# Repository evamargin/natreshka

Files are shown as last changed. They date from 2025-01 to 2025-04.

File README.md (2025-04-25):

# Natreshka - Neuropixels 2.0 implant ([pdf](https://github.com/evamargin/natreshka/blob/main/Natreshka%20-%20Neuropixels%202.0.pdf))

## 1. Introduction

**Natreshka** is an open-source implantation system designed for Neuropixels 2.0, offering a secure, modular, and user-friendly solution for chronic recordings. The implant is lightweight (3.8 g), compact (14.6 × 14.2 × 26 mm), and fully 3D-printable, requiring only standard M1/M3 screws and nuts. Beyond its minimalistic design, Natreshka enables easy manual implant assembly, fast and precise implantation under different angles, manual **stereotax-free** probe recovery, and protected storage of assembled probes (Fig. 1). Successfully tested in freely moving gerbils and rats, Natreshka streamlines implantation procedures, reduces surgery time, and enhances animal welfare, making it an efficient and accessible tool for neuroscience research.

This guide will take you through every step - from printing and assembling to implantation and recovery - while highlighting pitfalls and offering practical tips for a smooth operation.

<p align="center">
  Figure 1
</p>

**Figure 1.** Our view.

- [1. Introduction](#1-introduction)
- [2. Materials and equipment](#2-materials-and-equipment)
  - [2.1. List of printed and sourced parts](#21-list-of-printed-and-sourced-parts)
    - [2.1.1. Parts list (3D printed)](#211-parts-list-3d-printed)
    - [2.1.2. Parts list (non-printed)](#212-parts-list-non-printed)
  - [2.2 Tools Required](#22-tools-required)
    - [2.2.1. Recommended 3D printers, filaments](#221-recommended-3d-printers-filaments)
    - [2.2.2. Assembly tools](#222-assembly-tools)
- [3. 3D printing the components](#3-3d-printing-the-components)
  - [3.1. 3D printing setting](#31-3d-printing-setting)
  - [3.2. Post-Printing Processing](#32-post-printing-processing)
- [4. Natreshka’s lifecycle](#4-natreshkas-lifecycle)
  - [4.1. Build a payload](#41-build-a-payload)
  - [4.2. Assemble](#42-assemble)
    - [4.2.1. Prepare the parts](#421-prepare-the-parts)
    - [4.2.2. Assemble the implant](#422-assemble-the-implant)
    - [4.2.3. Prepare the cable](#423-prepare-the-cable)
  - [4.3. Implant](#43-implant)
  - [4.4. Record](#44-record)
  - [4.5. Recover](#45-recover)
    - [4.5.1. Clean](#451-clean)
  - [4.6. Store](#46-store)

## 2. Materials and equipment

### 2.1. List of printed and sourced parts

<p align="center">
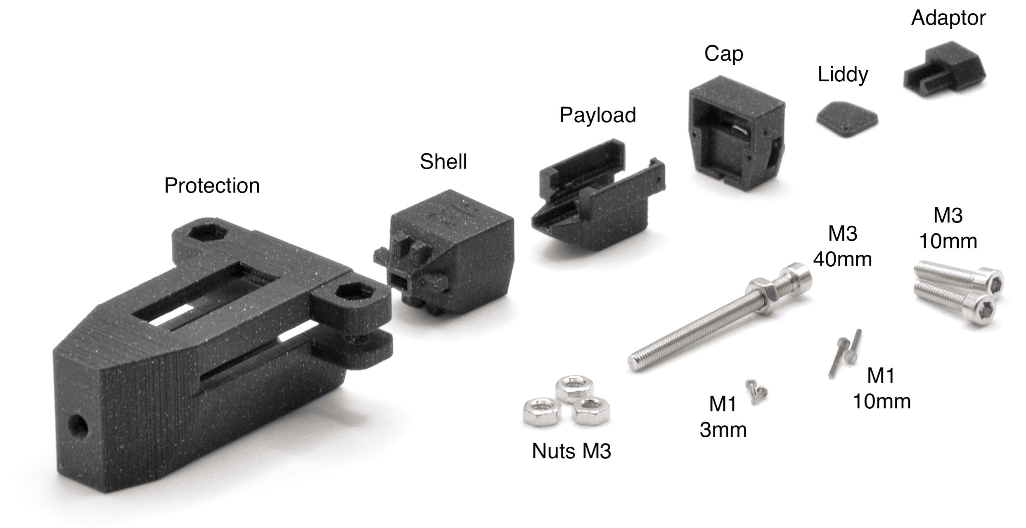
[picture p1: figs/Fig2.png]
Figure 2
  
</p>

**Figure 2.** Parts overview.

#### 2.1.1. Parts list (3D printed)

- [Payload](payload.stl)
- [Shell](shell.stl)
- [Cap](cap.stl)
- [Liddy](liddy.stl)
- [Cable adaptor](adapter.stl)
- [Protection](protection.stl)

#### 2.1.2. Parts list (non-printed)

| Name            | Description                                                                            | Quantity | Vendor                                                                                           |
| --------------- | -------------------------------------------------------------------------------------- | -------- | ------------------------------------------------------------------------------------------------ |
| Nuts M3         | DIN 934, hexagon type (6KT), A2 stainless steel                                        | 4        | [link](https://ghw-modellbau.de/DIN-934-6KT-Mutter-Edelstahl-A2-blank-M3-50-Stk)                 |
| Screw M3 40 mm  | DIN 912, cylinder head with ISK (hexagon socket / Allen key) drive, A2 stainless steel | 1        | [link](https://ghw-modellbau.de/DIN-912-Zylinderkopf-Schraube-Edelstahl-A2-blank-M3-x-30-50-Stk) |
| Screws M3 10 mm | DIN 912, cylinder head with ISK (hexagon socket / Allen key) drive, A2 stainless steel | 2        | [link](https://ghw-modellbau.de/DIN-912-Zylinderkopf-Schraube-Edelstahl-A2-blank-M3-x-30-50-Stk) |
| Screws M1 10 mm | DIN 84, cylinder head with SZ (slot) drive, A2 stainless steel                         | 2        | [link](https://ghw-modellbau.de/DIN-84-Zylinderkopf-Schraube-Edelstahl-A2-blank)                 |
| Screws M1 3 mm  | DIN 84, cylinder head with SZ (slot) drive, A2 stainless steel                         | 2        | [link](https://ghw-modellbau.de/DIN-84-Zylinderkopf-Schraube-Edelstahl-A2-blank)                 |

### 2.2. Tools Required

#### 2.2.1. Recommended 3D printers, filaments

- High-precision 3D extrusion printer (we used [Prusa MINI](https://www.prusa3d.com/product/original-prusa-mini-semi-assembled-3d-printer-enclosure-bundle/) with a classic [smooth sheet](https://www.prusa3d.com/product/smooth-pei-print-sheet/) and 0.25 nozzle)
- PLA printing material (we used [Prusament PLA Prusa Galaxy Black](https://www.prusa3d.com/product/prusament-pla-prusa-galaxy-black-1kg/))

#### 2.2.2. Assembly tools

- holder (for payload assembly)
- micro screwdriver (for M1 screws)
- hex key size 2.5 (for M3 screws)
- spanner size 5.5 (for M3 nuts)
- forceps (for handling the probe, cleaning 3D printed parts, etc)
- syringe needles d=0.9 (for cleaning 3D printed parts)
- epoxy (for gluing the probe to the payload)

<p align="center">
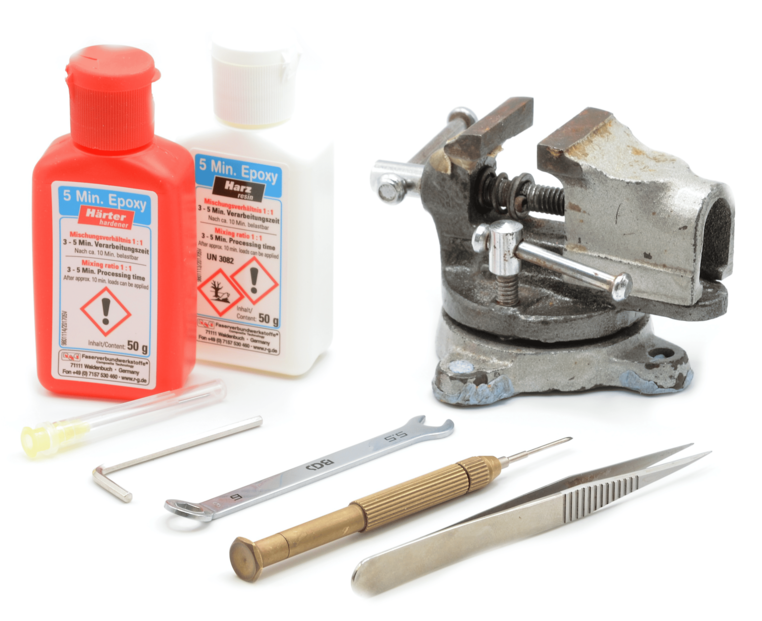
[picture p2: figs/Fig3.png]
Figure 3
  
</p>

**Figure 3.** Tools overview.

## 3. 3D printing the components

### 3.1. 3D printing setting

The position of the details is important (see Fig. 4). Printing settings are available as a G-code (link).

<p align="center">
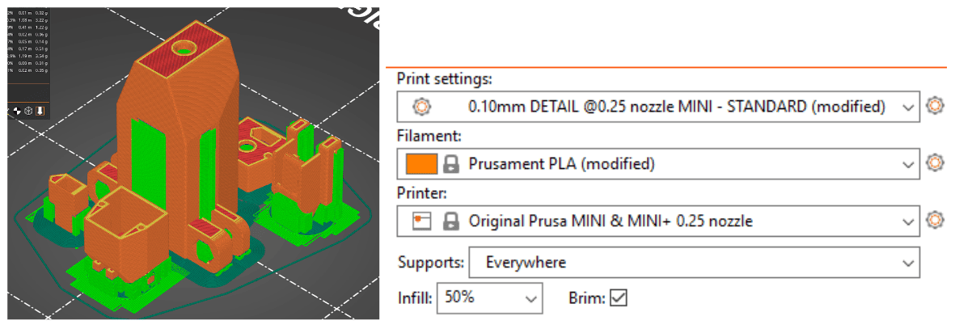
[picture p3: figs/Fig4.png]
Figure 4
  
</p>

**Figure 4.** Settings for 3D printing of the implant parts.

### 3.2. Post-Printing Processing  

<p align="center">
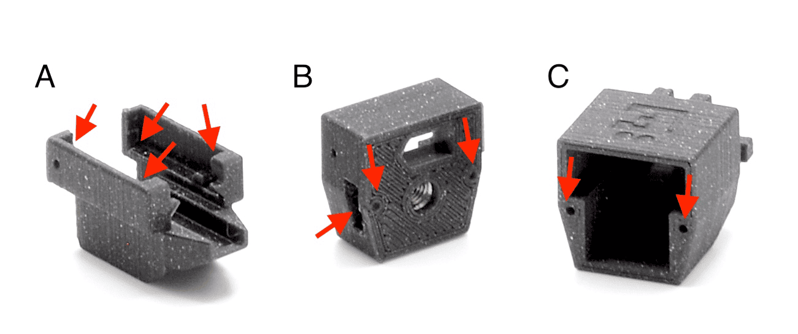
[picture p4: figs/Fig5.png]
Figure 5
  
</p>

**Figure 5.** Cleaning of the 3D printed parts.

- Remove all printing supports using forceps. 
- Ensure proper cleaning of the inner corners of the payload balcony (see Fig. 5A).
- Clean the cap and the shell holes (shown in Fig. 5B, 5C) using a needle (d=0.9). Leave the other holes as it is to maintain screw grip.
- Clean out the M3 nut slot in the cap (Fig. 5B) using sturdy forceps. This area is tricky - make sure you clean it properly.

**Tip #1:** If parts don’t fit properly (e.g., M3 nuts in the protection), check that all support material has been thoroughly removed. Incomplete cleaning is a common cause of misalignment.

**Tip #2:** Print quality matters. All surfaces should be smooth, and the payload should slide into the shell easily. Sometimes, one needs to slide details in and out several times to break them in. If it still catches, consider reprinting with a higher resolution.

**Tip #3:** Check that all printed parts have straight walls where intended. When the payload is placed in the shell and covered with the cap, the gap between the shell and cap should be uniform. If there are large deviations, reprint the affected part.

## 4. Natreshka's lifecycle

### 4.1. Build a payload

<p align="center">
  Figure 6
</p>

**Figure 6.** Building a payload step by step.

1. Fix the payload in the holder (Fig. 6A).
2. Apply epoxy to the surface where the probe will be mounted.
3. Remove the probe from its case and place it onto the glued area (Fig. 6B).
4. Gently press on the metal/silicone cap to ensure even contact.
5. Wait ~5 minutes for the glue to set.
6. Remove the payload from the holder, flip it upside down, and fix it back in (Fig. 6C).
7. Apply tape to the holder to protect the shanks (Fig. 6D).
8. Route the flex cable under the plastic beam (Fig. 6E).
9. Connect the headstage to the flex cable (Fig. 6F).
10. Insert the headstage into the payload balcony from the back, gently bending the flex cable (Fig. 6G).

**Tip #4:** Don’t worry about bending the cable during assembly - the required bend won’t affect signal quality or long-term stability.

**Tip #5:** In this design, the ground wire connects directly to the headstage, not the flex cable (Fig. 7). Solder it to the headstage ground pad in advance. This setup has been tested and works reliably.

**Tip #6:** The headstage should fit precisely into the payload and sit tight. If you feel some squeeze, remove the payload and thoroughly clean any 3D-printing residue from its corners before trying again. Precise placement of the headstage is very important to get Omnetics connected in the assembled implant!

<p align="center">
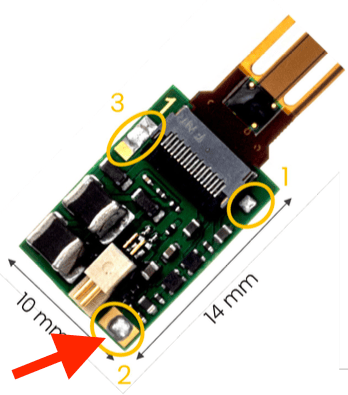
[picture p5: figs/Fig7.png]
Figure 7
  
</p>

**Figure 7.** The site for the ground wire connection on the headstage.

### 4.2. Assemble

#### 4.2.1. Prepare the parts

1. Insert two M3 nuts into the protection piece and screw in two M3 10 mm screws.
2. Insert one M3 nut into the cap from the side slot (Fig. 5B).

#### 4.2.2. Assemble the implant


**Figure 8.** Implant assembly step by step.

1. Fix the shell in the protection tightening the protection screws (Fig. 8A).
2. Insert manually the assembled payload into the shell (Fig. 8B).
3. Pre-screw the M1 3 mm screws into the side holes of the cap and M1 10mm screws on the top of the cap. Don’t forget to attach the liddy (Fig. 8C).
4. Close the shell, ensuring the ground wire sits in the groove in the cap wall (Fig. 8C).
5. Fully tighten the M1 3 mm screws to secure the cap to the payload (Fig. 8D).
6. Fully tighten the M1 10 mm screws to connect the shell and cap (Fig. 8D).
7. Loosen the protection screws, push the implant fully in, and re-tighten them. This way, the implant can be safely stored (Fig. 8E). 

#### 4.2.3. Prepare the cable 

<p align="center">
  Figure 9
</p>

**Figure 9.** Adaptor assembly.

1. Thread the Omnetics cable through the adaptor (Fig. 9A).
2. Plug the Omnetics connector into the headstage via the adaptor hole in the cap (Fig. 9B).
3. Apply a small amount of glue to the groove of the adaptor (Fig. 9B).
4. Plug the adaptor into the adaptor hole in the cap (Fig. 9C).
5. Wait ~5 minutes for the glue to set.
6. Gently unplug the adaptor from the implant (Fig. 9D).
7. Apply more glue to the outer side of the adaptor to secure the cable.
8. Once dry, test re-plugging the adaptor. If it doesn’t fit due to excess glue, file it down slightly.

**Tip #7:** Avoid using too much glue in Step 3 - it can damage the connector or headstage. If available, optically curable dental cement can be used here: apply, plug in the adaptor, and cure with UV. However, for Steps 5 and 6, superglue is better - dental cement may not bond well to plastic.

**Tip #8:** If you prefer using the Omnetics cable instead of the classic Neropixel twisted pair, you can make an adaptor from 4-pin Omnetics to 12-pin Omnetics (Fig. 10)

<p align="center">
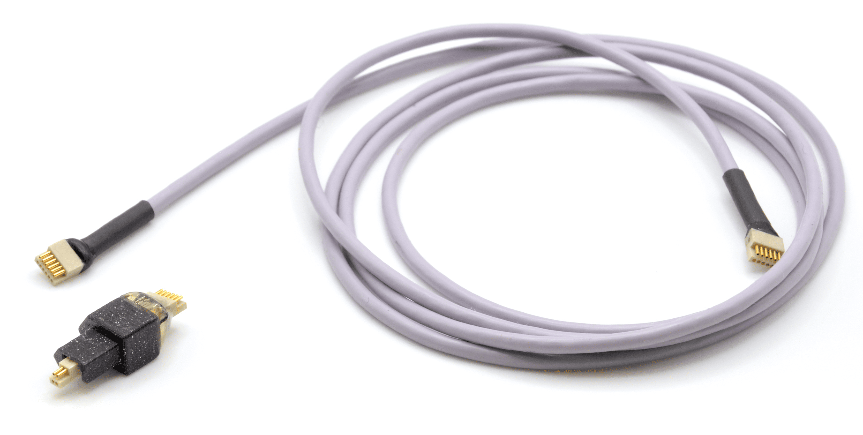
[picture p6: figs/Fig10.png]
Figure 10
  
</p>

**Figure 10**. 4 to 12 pins Omnetics adaptor.

## 4.3. Implant

To fix the implant in a stereotax, we place M3 40mm screw in the cap (Fig. 11) and atteach it to a custom holder. 

<p align="center">
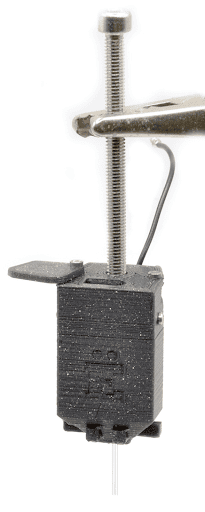
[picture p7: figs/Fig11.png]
Figure 11
  
</p>

**Figure 11.** Fully assembled probe ready for the implantation. 

**Tip #9:** Test the assembled probe before the implantation: connect it to the system to confirm it's detected. Detection might fail if the headstage and the flex cable were not connected properly.

**Tip #10:** Use Vaseline to seal the window where the shanks exit the implant. 

## 4.4. Record

- Gently restrain the animal, open the lid, and plug in the adapter to begin recording.
- When finished, unplug it and close the lid to protect the headstage and connector.

## 4.5. Recover

<p align="center">
  Figure 12
</p>

**Figure 12.** Probe recovery step by step.

1. Anesthetize the animal.
2. Unscrew the M1 10 mm screws from the cap and remove the liddy (Fig. 12A). 
3. Attach the protection piece as shown in Fig. 12B.
4. Prepare the M3 40 mm screw by placing an M3 nut onto it.
5. Insert the screw through the hole in the protection and thread it into the central hole in the cap Fig. 12C).
6. Gently pull the nut downward using a spanner Fig. 12D). As the nut moves down relative to the screw, the payload (with the cap) will slowly rise out of the shell.
7. Once the shanks are fully retrieved, lift the protection with the probe vertically (Fig. 12E).
8. Transfer the payload with a cap attached into the new cap (Fig. 12F), repeating the process described in 4.2.2 Assemble the implant.

### 4.5.1. Clean

<p align="center">
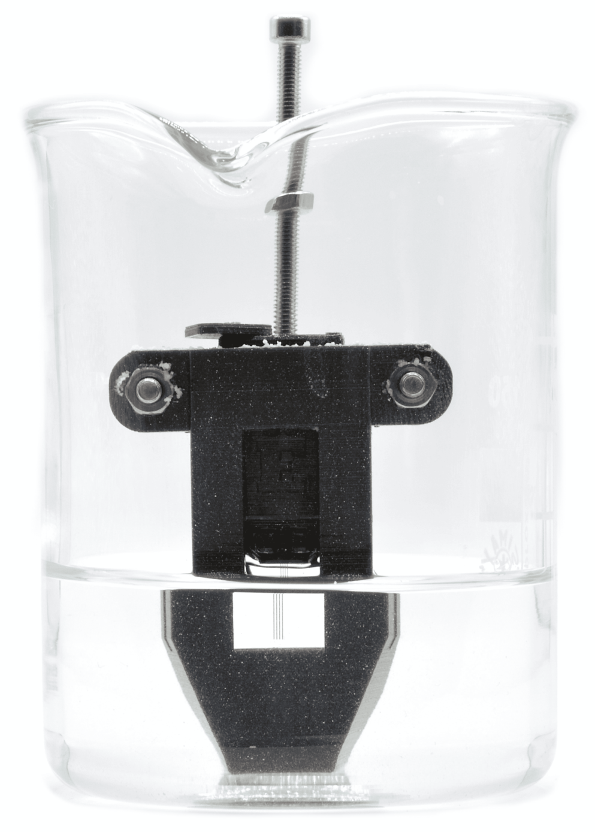
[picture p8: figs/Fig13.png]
Figure 13
  
</p>

**Figure 13.** Cleaning the recovered probe.

1. Fix the implant in the protection in the elevated position to enable the opening of the liddy.
2. Screw the M3 40mm screw into the cap to handle the construction easier.
3. Prepare the solution for the probe cleaning (we use tergazyme for Stage 1 and isopropyl for Stage 2).
4. Place the probe in the glass with the cleaning solution (Fig. 13).

**Tip #11:** Be careful with the amount of cleaning solution. It should cover the shanks but not reach the level of the headstage.

## 4.6. Store

To store the probe safely, insert the assembled implant fully into the protection and tighten the M3 10 mm screws on the protection (Fig. 8E).

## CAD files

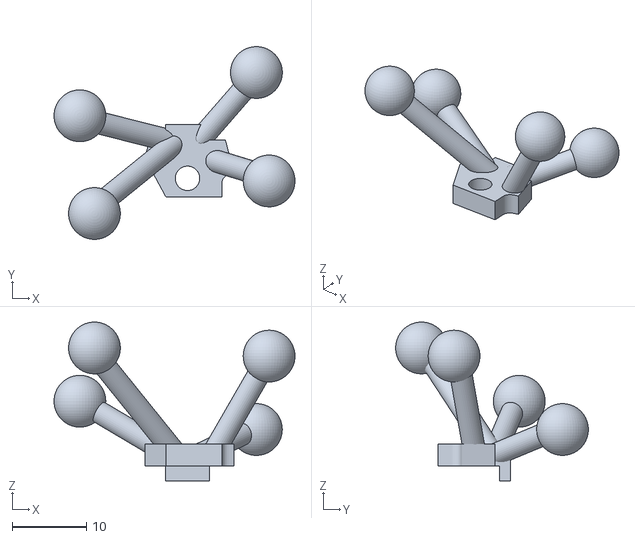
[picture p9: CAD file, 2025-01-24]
accessories/optitrack.stl
32.6 x 26.0 x 21.5

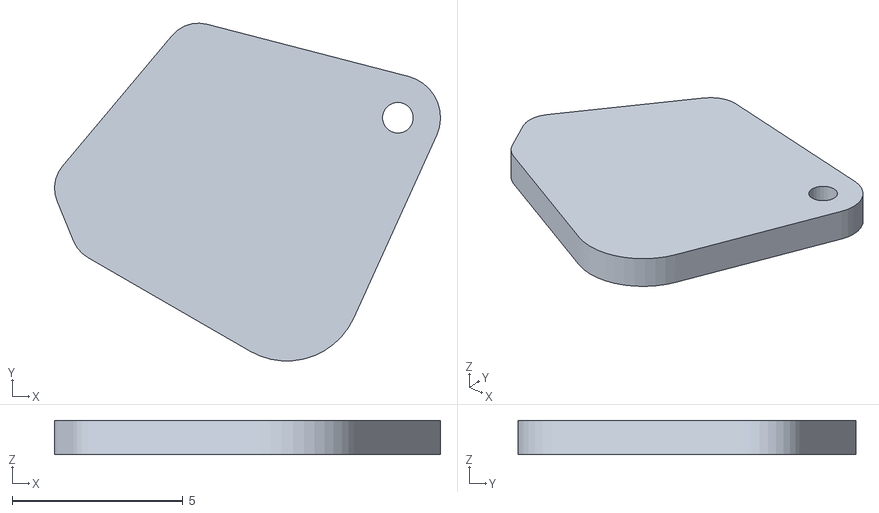
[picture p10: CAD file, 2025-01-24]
liddy.stl
11.3 x 9.90 x 1.00

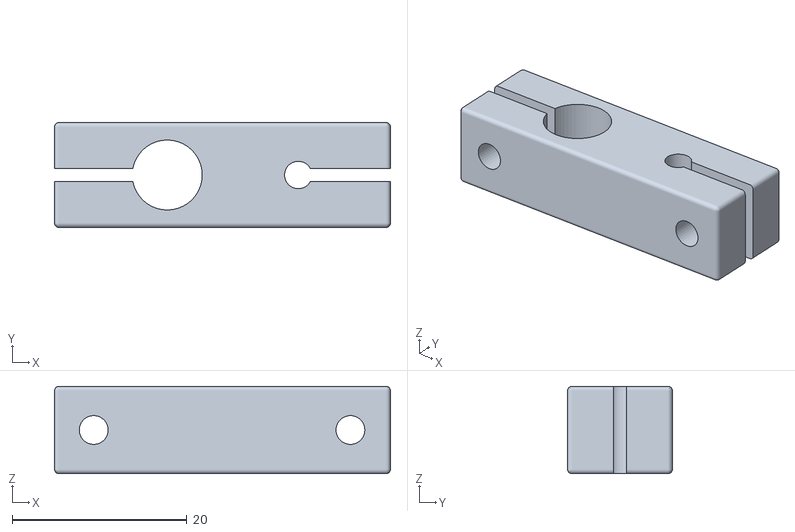
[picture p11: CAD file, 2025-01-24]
accessories/steretaxic_holder.stl
38.5 x 12.0 x 10.0

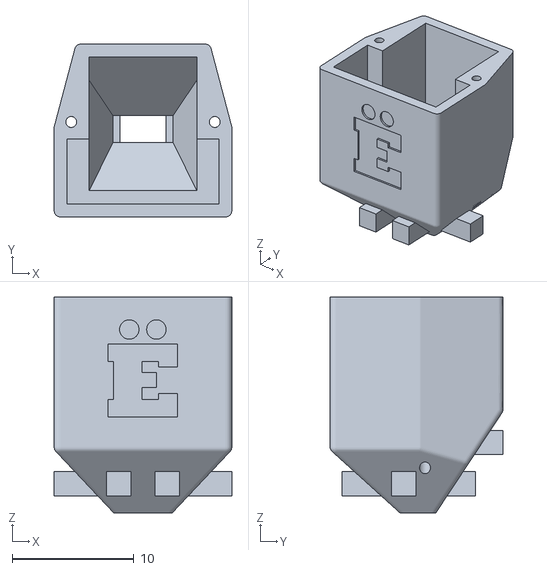
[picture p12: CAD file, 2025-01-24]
shell.stl
14.6 x 14.2 x 17.8

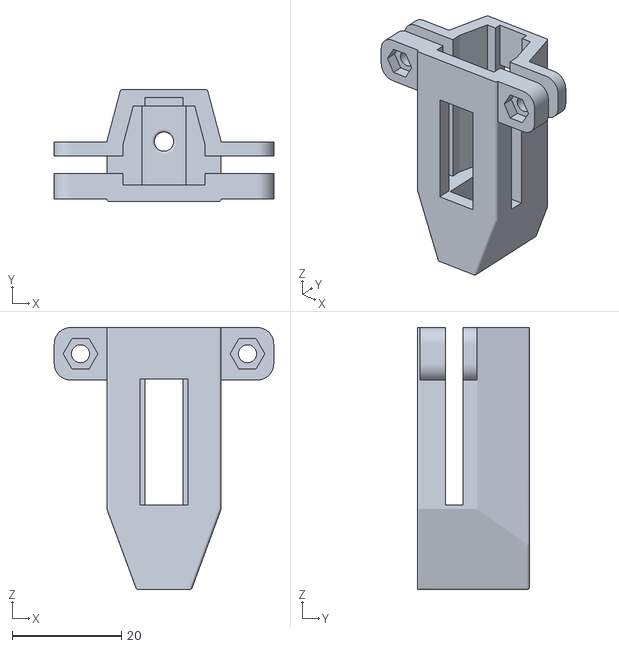
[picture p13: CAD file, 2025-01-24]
protection.stl
40.1 x 20.5 x 47.9

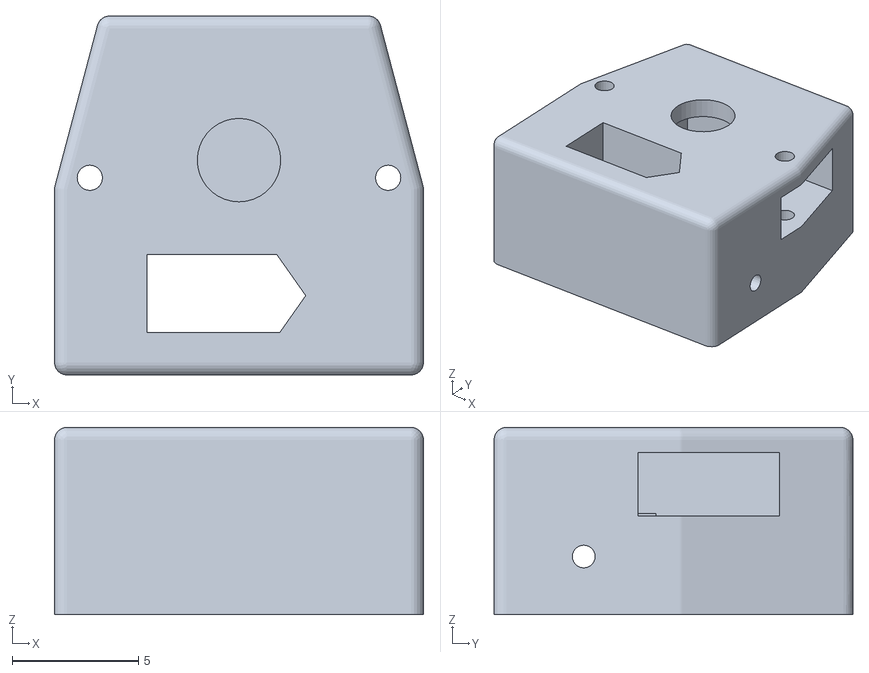
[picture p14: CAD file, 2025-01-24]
cap.stl
14.6 x 14.2 x 7.41

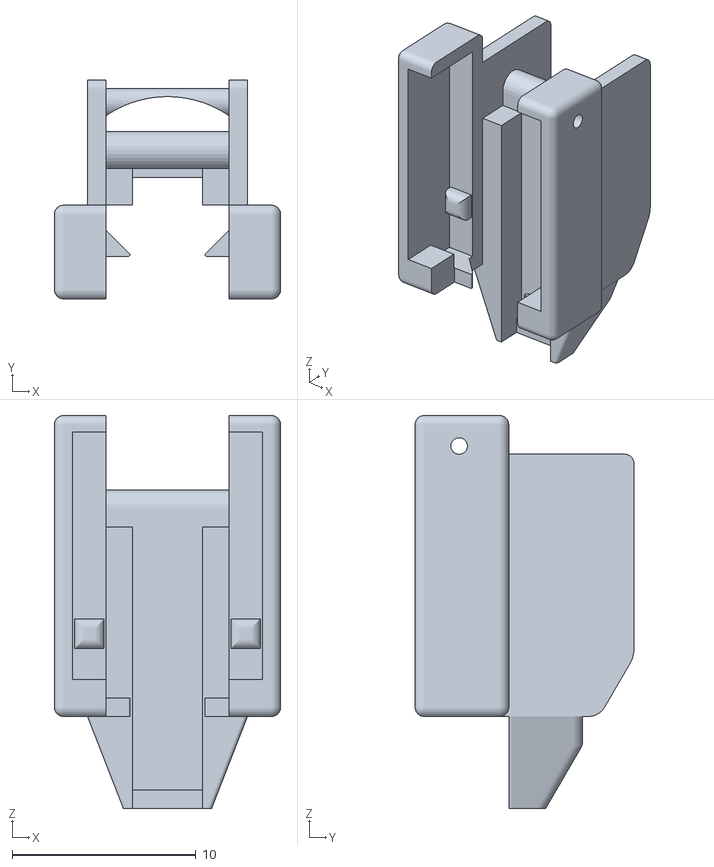
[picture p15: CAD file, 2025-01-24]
payload.stl
12.3 x 11.9 x 21.4

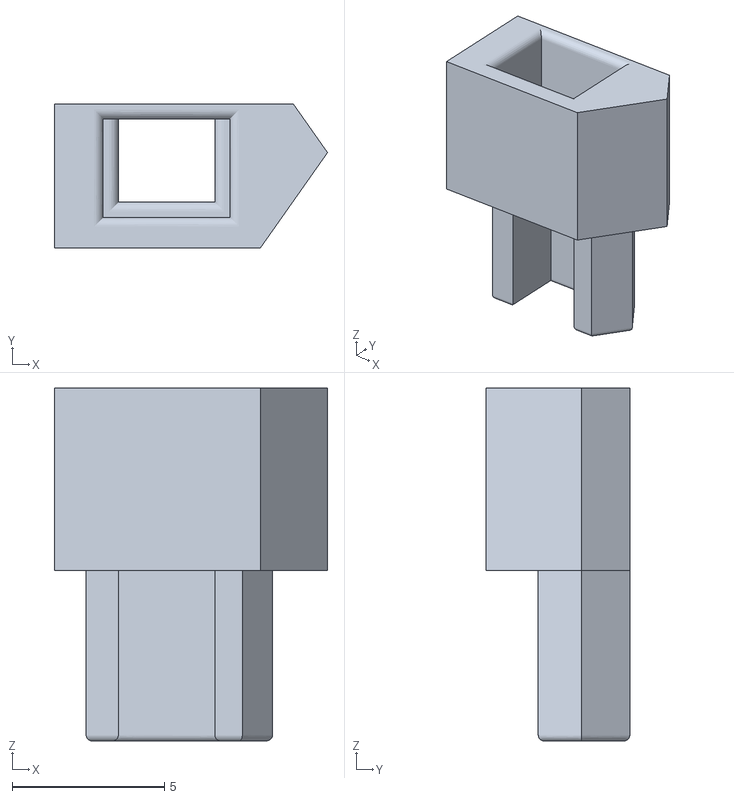
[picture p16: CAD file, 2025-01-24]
adapter.stl
8.97 x 4.72 x 11.6

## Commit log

2025-01-23 version 1.0
    [adapter.stl, cap.stl, liddy.stl, optitrack.stl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]
2025-01-23 changed orientation of shell
    [shell.stl]
2025-01-23 changed orientation of shell - 2
    [shell.stl]
2025-01-23 changed orientation of everything
    [adapter.stl, cap.stl, liddy.stl, optitrack.stl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]
2025-01-24 fixed wrong STL sizes
    [adapter.stl, cap.stl, liddy.stl, optitrack.stl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]
